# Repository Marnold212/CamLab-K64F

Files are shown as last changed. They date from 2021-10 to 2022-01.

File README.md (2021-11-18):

# CamLab-K64F
Code for performing data acquisition with the FRDM-K64F microcontroller. Currently tested using Windows 10 and VS Code. 

## Cloning Git Repo

Since mbed-os folder is linked as a submodule, in order to compile code locally, you must use the command "git clone --recursive https://github.com/Marnold212/CamLab-K64F" to also clone the mbed-os from its respective repo.  

## Flashing correct mbed Bootloader to K64F 

This may be need to be done for a new board, or a board that was previously used with a different program such as NXP MCUXpresso. Also may be required if there is a memory issue which crashes the board. Follow instructions on https://daplink.io/?board=FRDM-K64F.

- Copy of bootloader .bin file which is saved in the main branch of this repository 
- Reset button on K64F while connecting to PC via USB - should mount as bootloader 
- Drag and drop the .bin firmware file to the board and wait roughly 60 seconds
- unplug and should now have the correct firmware 

## Windows Toolchain 

Breif description of tools required for this project  

- **Git** https://git-scm.com/download/win
- **Python 3.9** was the version I used - Can use a Virtual Environment
  - Note that on powershell I needed to enable scripts (see below)
- **mbed-CLI 1** since mbed-CLI2 doesn't seem to have the same feature set 
- **GNU Arm Embedded Toolchain** version depends on which mbed-CLI version is used can be found on mbed-CLI documentation
  - Note that path must be specified in mbed config 
  - Name slightly for different versions - beware if changing path names 

## Installing GNU Arm Embedded Toolchain

On windows download .exe from https://developer.arm.com/tools-and-software/open-source-software/developer-tools/gnu-toolchain/gnu-rm/downloads for correct major version - Currenty latest supported is v9 2019-q4-major. Run the .exe file and select the add to PATH option in the installer. Check path of installation specifically the bin file as this path will be required. 

## Installing mbed-CLI 1

Use the package manager [pip](https://pip.pypa.io/en/stable/) to install mbed command line tools for compiling and flashing mbed device. Note that special instructions required to install mercurial with a venv(virtual environment) due to Visual C++ requirement - see below. 

```bash
pip install mbed-cli
pip install mbed-greentea
pip install mercurial
pip install mbed-ls
pip install mbed-tools
```

## Installing required packages for mbed-CLI 1
mbed-cli has a number of dependencies which are required for various tasks such as compiling. One way to install these is to import either an example program or just mbed-os as described below. Within root directory of mbed-os/ there is a requirements.txt file so 'pip install (-U) -r requirements.txt' should work otherwise can install manually. When trying to compile a project it should list any missing packages, although this method may lead to issues with versions and dependencies. 

## Basic mbed-CLI Usage 

mbed-CLI runs in command-line such as a vs-code terminal or windows CMD. Look at the documentation for [mbed-CLI 1](https://os.mbed.com/docs/mbed-os/v6.15/build-tools/mbed-cli-1.html) for further details. Note that to my knowledge pyOCD does not work on Raspberry Pi architechture so tools such as flashing board or debugging don't work.

Note that compiling a project for the 1st time will take a very long time due to the number of libraries in mbed-os which need to be compiled, however the 2nd time will be much quicker, as only modified classes need to be recompiled. 

```python
# lists available commands 
mbed 

# After cloning this project, may need to create a local mbed project within folder 
mbed new . 

# set the path for the GCC Toolchain - this path depends on your installation 
mbed config --global GCC_ARM_PATH "C:\Program Files (x86)\GNU Arm Embedded Toolchain\10 2020-q4-major\bin"

# returns list of connected devices 
mbed detect

# returns current compilation config 
mbed config --list

# set local toolchain to GCC_ARM (Use -G flag for global config)
mbed -t GCC_ARM

# set local device to either detect or k64f (Use -G flag for global config)
mbed -m detect
mbed -m k64f

# imports example project 
mbed import https://github.com/ARMmbed/mbed-os-example-blinky 

# imports mbed-os library
mbed import mbed-os 

# Compile an mbed project (-t and -m not required if aready set within project)
# -f flag automatically flashes .bin file if there is a suitable device connected 
# --sterm option opens a terminal in the command line with default settings (9600)
mbed compile -t <toolchain> -m <target> -f --sterm 
```

## Python Virtual Environments (venv)

To avoid clashes with dependencies, create a virtual environment. Activate the venv by running the activation script, exit by running "deactivate". 
There may be issues running the activation script using powershell due to permissions, if so use the command "Set-ExecutionPolicy Unrestricted -Scope Process". 

```bash
pyton -m venv venv 
pip list 
venv/Scripts/activate 
```

Had [issues](https://github.com/CodeForBuffalo/affordable_water/issues/11) installing mercurial using venv due to lack of Microsoft Visual C++ 14.0, even though I already had Microsoft Visual C++ 14 installed on PC. To solve, install build tools for Visual Studio from https://visualstudio.microsoft.com/downloads/, go to individual components and install: 
* Windows 10 SDK 
* C++ CMake Tools 
* MSVC (latest version) C++ x64/86 build tools 
* C++/CLI suppport 

## Debugging K64F 

The K64F has an on-chip debugger that allows debugging of program. The only configuration I have successfully implemented is pyOCD using VS Code as I couldn't get OpenOCD to work on this board. Install pyOCD using pip as shown below ensuring no issues with dependencies, and check it is working by running commands "pyocd list" or "pyocd-gdbserver" in CMD with the K64F connected. 

```bash
pip install pyOCD 
```
We now need to configure VS Code in order to allow us to run the debugger. 

## Configuring VS-Code 

Configuration for vs-code to allow for debugging of K64F as well as building of code without debugging which I use to save having to write command every time I compile code. Requires the following:
- VS Code Extensions
  - C/C++
  - cortex-debug (marcus25)
- Modification of the .vscode/ folder in the project directory 
  - launch.json
  - tasks.json 
  - c_cpp_properties.json

There a few different methods for adding a .vscode/ folder to a project. The easiest would be to modify the one in this reopository for particular computer, another option in vs code is to attempt "Run and Debug" without one it should create a template. Also you could use the mbed command "mbed export -i vscode_gcc_arm -m K64F --profile mbed-os/tools/profiles/debug.json".

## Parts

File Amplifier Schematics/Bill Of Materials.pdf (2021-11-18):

## Bill Of Materials for UKCRIC-NRFIS LabJack Extn Bd

Design Title | UKCRIC-NRFIS LabJack Extn Bd
Author | MW
Document Number | 2011101
Revision | B
Design Created | 15 April 2021

### Design Last Modified 15 April 2021 Total Parts In Design 129

31 Resistors
Quantity References | BOM Value Value | Tol | Package Description | Key
Properties
Manufacturer Manufacturer's PN | Supplier | Order
Code
2 | R1-R2 | 470R | 470R | 1% | 0805 | Thick Film SMTResistor 150V
Preferred | Panasonic | ERJ6ENF4701V | Farnell | 230-3515
3 | R3-R4,R7 | 0R | 0R | 5% | 0805 | Thick Film SMTResistor 150V
Panasonic | ERJ-6GEY0R00V | Farnell | 205-7661
2 | R5-R6 | 2k7 | 2k7 | 1% | 0805 | Thick Film SMTResistor 150V
Panasonic | ERJ6ENF2701V | Farnell | 230-3597
16 | R101-R102,R201-R202,R301- | 3k9 | 3k9 | 1% | 0805 | Thick Film | Preferred | Panasonic | ERJ6ENF3901V | Farnell | 230-3613
R302,R401-R402,R501-R502, | | | SMTResistor
R601-R602,R701-R702,R801- | | | 150V
R802
8 | R103,R203,R303,R403,R503,
R603,R703,R803
100R | 100R | 1% | 0805 | Thick Film
SMTResistor
150V
Preferred | Panasonic | ERJ6ENF1000V | Farnell | 230-3442

Sub-totals:
62 Capacitors
Quantity References | BOM Value Value | Tol | Package Description | Key
Properties
Manufacturer Manufacturer's PN | Supplier | Order
Code
2 | C1-C2 | 4u7 | 4.7u | 20% 1206 | 25V Multilayer
X7R
Kemet | C1206C475M3RACTU Farnell | 282-0941
2 | C3-C4 | 1u0 | 1u0 | 10% | 1206 | 100V Multilayer X7R
AVX | 12061C105KAT2A | Farnell | 165-7939
2 | C5-C6 | 100n | 100n | 10% 0805 | Ceramic 50V
| | | | | | X7R
Preferred | Kemet | C0805C104K5RAC | Farnell | 141-4664

16 | C101-C102,C201-C202,C301- | 1n0 | 1n0 | 5% | 0805 | 50V Ceramic | Kemet | C0805C102J5GACTU | Farnell | 141-4658
C302,C401-C402,C501-C502, | | | COG
C601-C602,C701-C702,C801-
C802
16 | C103,C105,C203,C205,C303,
C305,C403,C405,C503,C505,
C603,C605,C703,C705,C803,
C805
10n | 10n | 10% 0805 | Ceramic 50V
X7R
Kemet | C0805C103K5RAC | Farnell | 141-4662
16 | C104,C106,C204,C206,C304, | 330n | 330n | 10% | 0805 | Ceramic 50V | Kemet | C0805C334K5RACTU | Farnell | 233-2405
C306,C404,C406,C504,C506, | | | X7R
C604,C606,C704,C706,C804,
C806
8 | C107,C207,C307,C407,C507,
C607,C707,C807
47n | 10% | Kemet | C0805C473K5RAC | Farnell | 141-4697

Sub-totals:
12 Integrated Circuits
Quantity References | BOM Value Value | Tol | Package Description | Key
Properties
Manufacturer Manufacturer's PN | Supplier | Order
| | | | | Code
1 | U1 | 5V-
>+5V,-5V
NTA0505MC | 10-pin
SMT

DC/DC
Converter
| | Murata | NTA0505MC | Farnell | 102-1591
1 | U2 | 5V-
>+12V,-12V
NTA0512MC | 10-pin
SMT

DC/DC
Converter
| | Murata | NTA0512MC | Farnell | 102-1593
2 | U3-U4 | Quad | SN74HCT125M | 14-pin
SOIC

Tristate buffer VIH >
2.0V
| | Texas Instruments | SN74HCT125M | Farnell | 312-1014
8 | U101,U201,U301,U401,U501,
U601,U701,U801
Precision | AD623ARZ | 8-pin
SOIC

Instrumentation
Amp
| | Analog Devices | AD623ARZ | RS Components | 806-5522

Sub-totals:
4 Wound Components
Quantity References | BOM Value Value | Tol | Package Description | Key
Properties
Manufacturer Manufacturer's PN | Supplier | Order
| | | | | Code
2 | L1-L2 | 10uH | SMT | 500mA Power
Inductor
| | Murata | 82103C | Farnell | 284-0105
2 | L3-L4 | 47uH | SMT | 250mA Power
Inductor
| | Murata | 82473C | Farnell | 211-2805

Sub-totals:
12 Connectors
Quantity References | BOM Value Value | Tol | Package Description | Key
Properties
Manufacturer Manufacturer's PN | Supplier | Order
| | | | | Code
1 | J1 | 40-way | M20-9982045 | 0.1"
pitch
dual row}
Pin header | Harwin | M20-9982045 | Farnell | 322-6016

1 | J2 | 16-way | M20-9980845 | 0.1"
pitch
dual row
Pin header | Harwin | M20-9980845 | Farnell | 102-2239
2 | J3-J4 | 15-pin | 171-015-113R911 | 15-pin Vertical
D-SUB Male | Norcomp | 171-015-113R911 | RS
Components

174-8712

8 | J101,J201,J301,J401,J501, J601,J701,J801 | 15-pin | 171-015-213R911 | 15-pin Vertical
D-SUB Female | Norcomp | 171-015-213R911 | RS
Components

174-8730

Sub-totals:
8 Miscellaneous
Quantity References | BOM Value Value | Tol | Package Description | Key
Properties
Manufacturer Manufacturer's PN | Supplier | Order
Code
2 | FU1-FU2 | 250mA | 0ZCJ0025FF2E | 1206 | SMT Fuse | Bel Power Solutions
0ZCJ0025FF2E | Farnell | 283-4885
3 | Z1,Z3,Z5 | | 0V | PCB feature
Test point | None | None | None | None
1 | Z2 | | PGND | PCB feature
Test point | None | None | None | None
1 | Z4 | | GND | PCB feature
Test point | None | None | None | None
1 | Z6 | | EARTH | PCB feature
Test point | None | None | None | None

Sub-totals:

Totals:

15 April 2021 13:20:37

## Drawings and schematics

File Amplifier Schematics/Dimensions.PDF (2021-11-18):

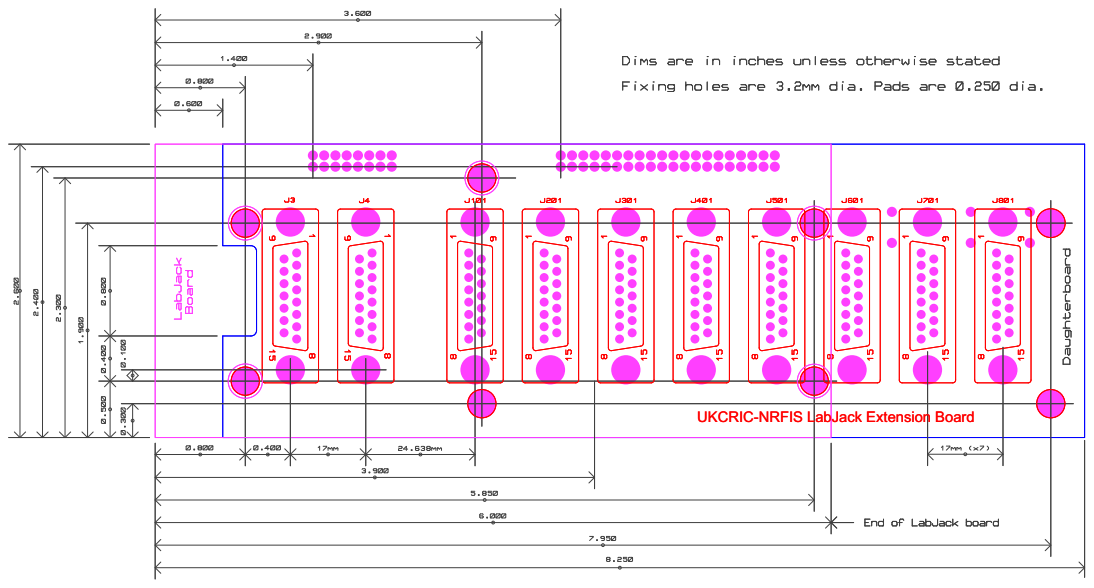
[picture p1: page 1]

UKCRIC-NRFIS LabJack Extension Board

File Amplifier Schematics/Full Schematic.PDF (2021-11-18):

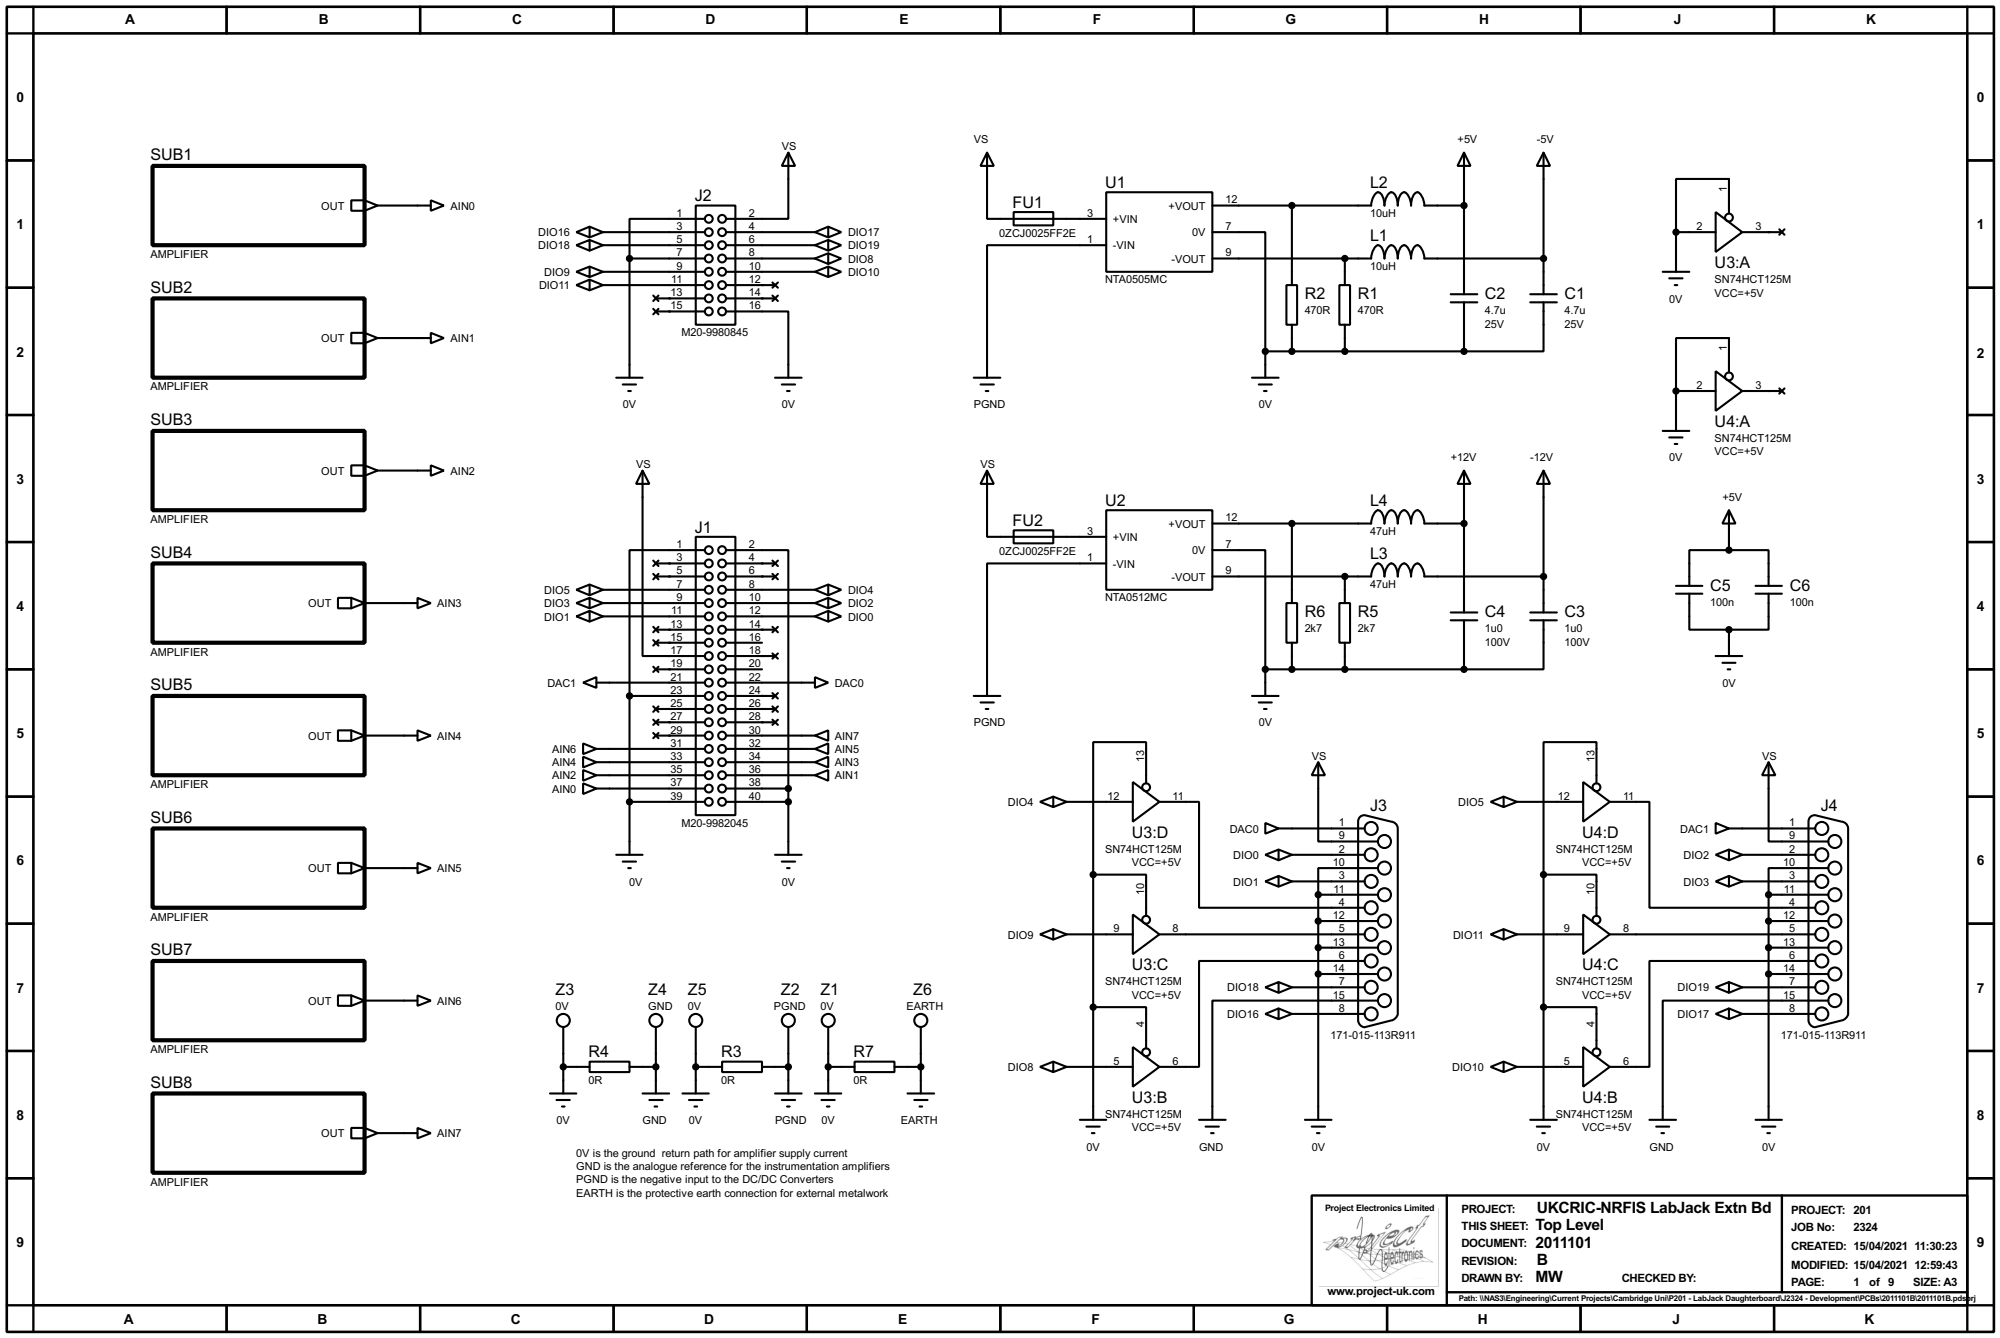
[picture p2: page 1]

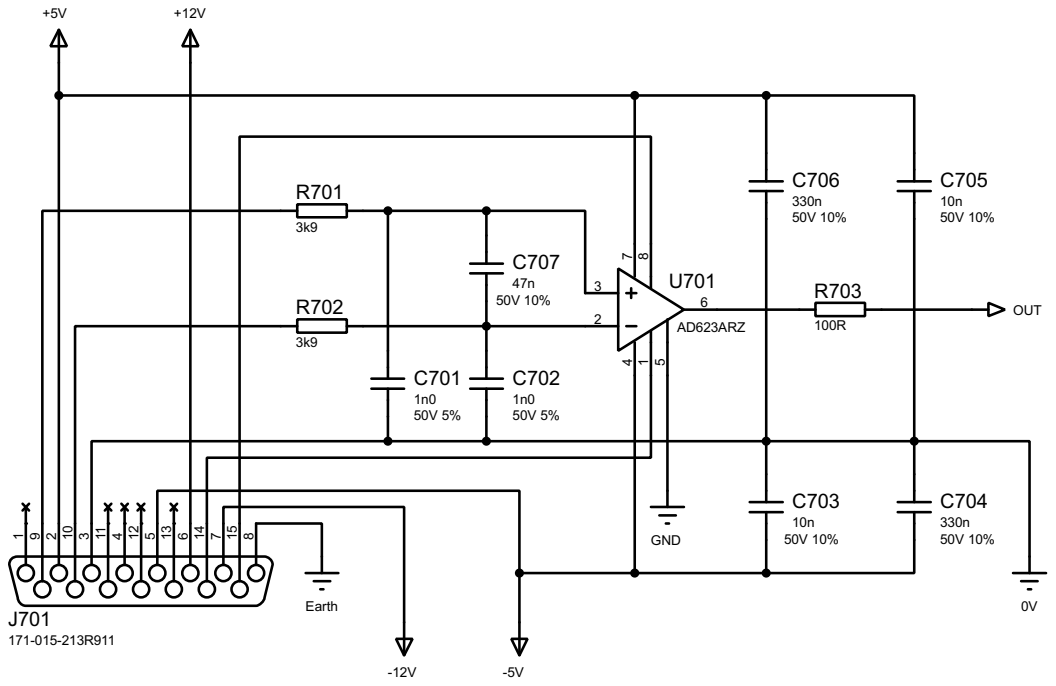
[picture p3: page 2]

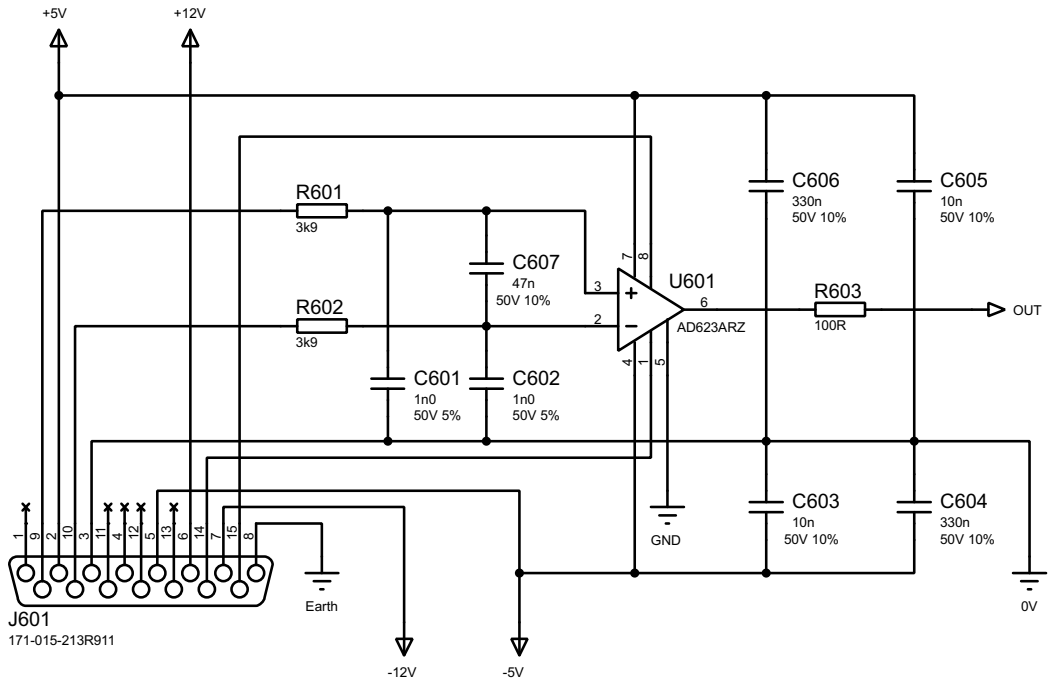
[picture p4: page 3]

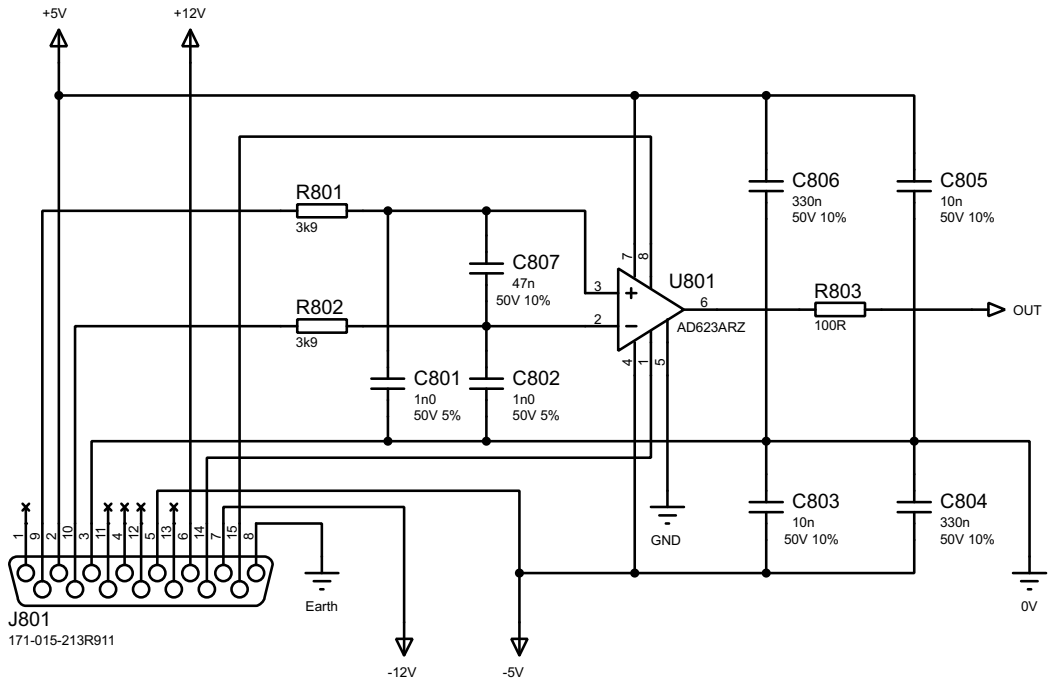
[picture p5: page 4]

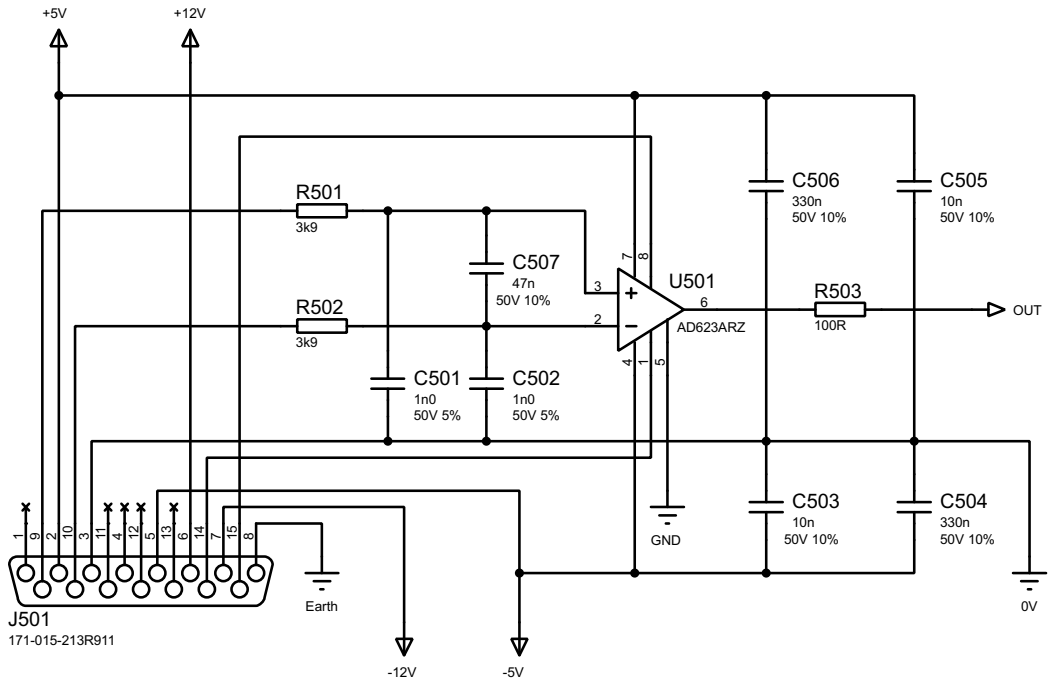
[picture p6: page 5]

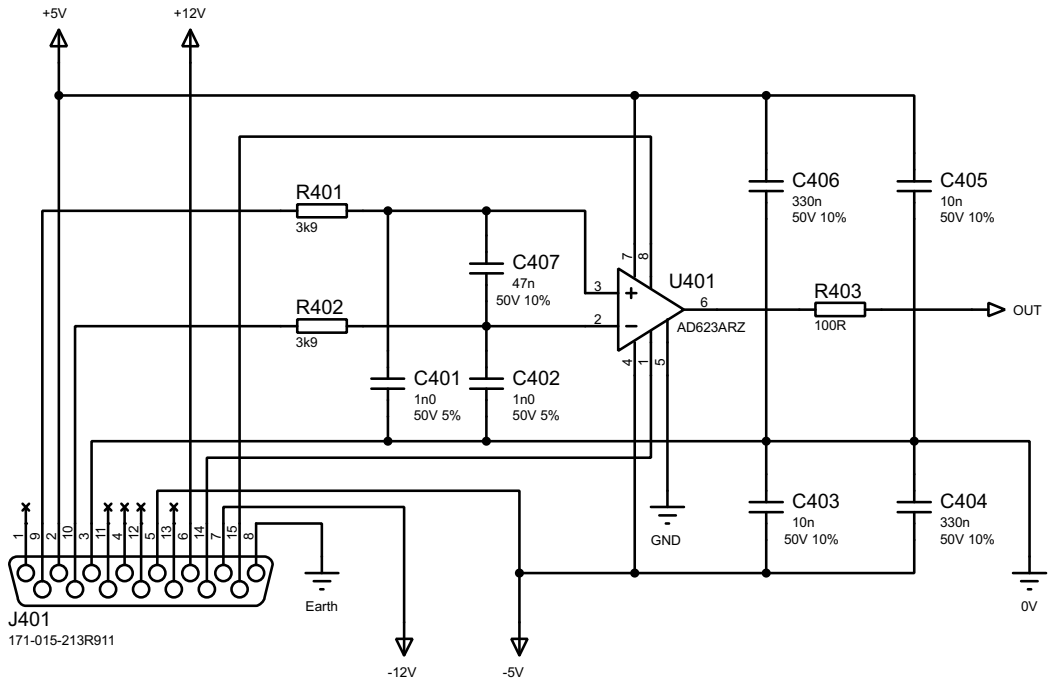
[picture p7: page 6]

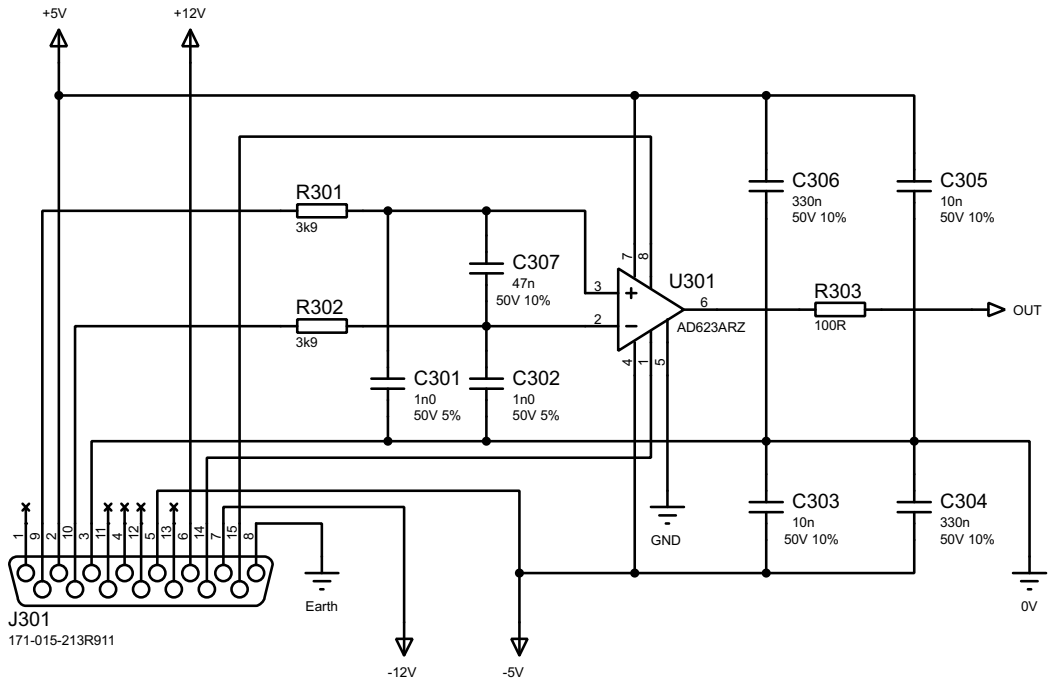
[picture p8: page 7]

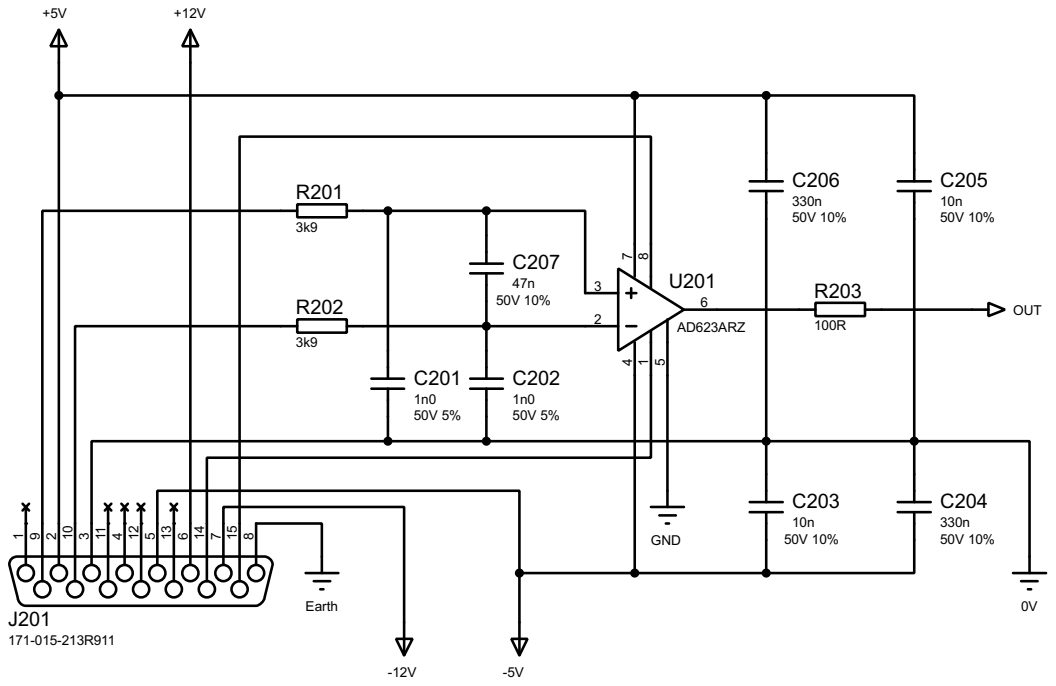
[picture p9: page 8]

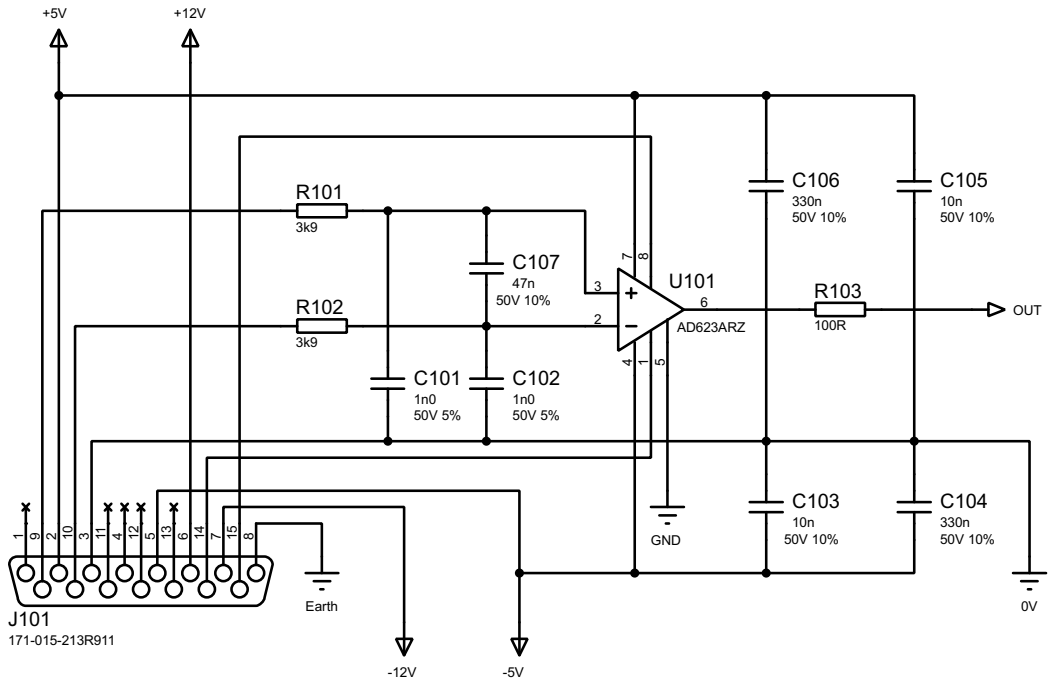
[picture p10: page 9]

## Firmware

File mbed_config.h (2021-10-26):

/*
 * mbed SDK
 * Copyright (c) 2017 ARM Limited
 *
 * Licensed under the Apache License, Version 2.0 (the "License");
 * you may not use this file except in compliance with the License.
 * You may obtain a copy of the License at
 *
 * http://www.apache.org/licenses/LICENSE-2.0
 *
 * Unless required by applicable law or agreed to in writing, software
 * distributed under the License is distributed on an "AS IS" BASIS,
 * WITHOUT WARRANTIES OR CONDITIONS OF ANY KIND, either express or implied.
 * See the License for the specific language governing permissions and
 * limitations under the License.
 */

// Automatically generated configuration file.
// DO NOT EDIT, content will be overwritten.

#ifndef __MBED_CONFIG_DATA__
#define __MBED_CONFIG_DATA__

// Configuration parameters
#define MBED_CONF_ALT1250_PPP_BAUDRATE                                        115200                                                                                           // set by library:ALT1250_PPP
#define MBED_CONF_ALT1250_PPP_PROVIDE_DEFAULT                                 0                                                                                                // set by library:ALT1250_PPP
#define MBED_CONF_ATMEL_RF_ASSUME_SPACED_SPI                                  0                                                                                                // set by library:atmel-rf
#define MBED_CONF_ATMEL_RF_FULL_SPI_SPEED                                     7500000                                                                                          // set by library:atmel-rf
#define MBED_CONF_ATMEL_RF_FULL_SPI_SPEED_BYTE_SPACING                        250                                                                                              // set by library:atmel-rf
#define MBED_CONF_ATMEL_RF_IRQ_THREAD_STACK_SIZE                              1024                                                                                             // set by library:atmel-rf
#define MBED_CONF_ATMEL_RF_LOW_SPI_SPEED                                      3750000                                                                                          // set by library:atmel-rf
#define MBED_CONF_ATMEL_RF_PROVIDE_DEFAULT                                    0                                                                                                // set by library:atmel-rf
#define MBED_CONF_ATMEL_RF_USE_SPI_SPACING_API                                0                                                                                                // set by library:atmel-rf
#define MBED_CONF_CELLULAR_AT_HANDLER_BUFFER_SIZE                             32                                                                                               // set by library:cellular
#define MBED_CONF_CELLULAR_CONTROL_PLANE_OPT                                  0                                                                                                // set by library:cellular
#define MBED_CONF_CELLULAR_DEBUG_AT                                           0                                                                                                // set by library:cellular
#define MBED_CONF_CELLULAR_MAX_CP_DATA_RECV_LEN                               1358                                                                                             // set by library:cellular
#define MBED_CONF_CELLULAR_PRESENT                                            1                                                                                                // set by library:cellular
#define MBED_CONF_CELLULAR_RANDOM_MAX_START_DELAY                             0                                                                                                // set by library:cellular
#define MBED_CONF_CELLULAR_USE_APN_LOOKUP                                     0                                                                                                // set by library:cellular
#define MBED_CONF_CELLULAR_USE_SMS                                            0                                                                                                // set by library:cellular
#define MBED_CONF_DRIVERS_OSPI_CSN                                            OSPI_FLASH1_CSN                                                                                  // set by library:drivers
#define MBED_CONF_DRIVERS_OSPI_DQS                                            OSPI_FLASH1_DQS                                                                                  // set by library:drivers
#define MBED_CONF_DRIVERS_OSPI_IO0                                            OSPI_FLASH1_IO0                                                                                  // set by library:drivers
#define MBED_CONF_DRIVERS_OSPI_IO1                                            OSPI_FLASH1_IO1                                                                                  // set by library:drivers
#define MBED_CONF_DRIVERS_OSPI_IO2                                            OSPI_FLASH1_IO2                                                                                  // set by library:drivers
#define MBED_CONF_DRIVERS_OSPI_IO3                                            OSPI_FLASH1_IO3                                                                                  // set by library:drivers
#define MBED_CONF_DRIVERS_OSPI_IO4                                            OSPI_FLASH1_IO4                                                                                  // set by library:drivers
#define MBED_CONF_DRIVERS_OSPI_IO5                                            OSPI_FLASH1_IO5                                                                                  // set by library:drivers
#define MBED_CONF_DRIVERS_OSPI_IO6                                            OSPI_FLASH1_IO6                                                                                  // set by library:drivers
#define MBED_CONF_DRIVERS_OSPI_IO7                                            OSPI_FLASH1_IO7                                                                                  // set by library:drivers
#define MBED_CONF_DRIVERS_OSPI_SCK                                            OSPI_FLASH1_SCK                                                                                  // set by library:drivers
#define MBED_CONF_DRIVERS_QSPI_CSN                                            QSPI_FLASH1_CSN                                                                                  // set by library:drivers
#define MBED_CONF_DRIVERS_QSPI_IO0                                            QSPI_FLASH1_IO0                                                                                  // set by library:drivers
#define MBED_CONF_DRIVERS_QSPI_IO1                                            QSPI_FLASH1_IO1                                                                                  // set by library:drivers
#define MBED_CONF_DRIVERS_QSPI_IO2                                            QSPI_FLASH1_IO2                                                                                  // set by library:drivers
#define MBED_CONF_DRIVERS_QSPI_IO3                                            QSPI_FLASH1_IO3                                                                                  // set by library:drivers
#define MBED_CONF_DRIVERS_QSPI_SCK                                            QSPI_FLASH1_SCK                                                                                  // set by library:drivers
#define MBED_CONF_DRIVERS_UART_SERIAL_RXBUF_SIZE                              256                                                                                              // set by library:drivers
#define MBED_CONF_DRIVERS_UART_SERIAL_TXBUF_SIZE                              256                                                                                              // set by library:drivers
#define MBED_CONF_ESP8266_BUILT_IN_DNS                                        0                                                                                                // set by library:esp8266
#define MBED_CONF_ESP8266_DEBUG                                               0                                                                                                // set by library:esp8266
#define MBED_CONF_ESP8266_POWER_OFF_TIME_MS                                   3                                                                                                // set by library:esp8266
#define MBED_CONF_ESP8266_POWER_ON_POLARITY                                   0                                                                                                // set by library:esp8266
#define MBED_CONF_ESP8266_POWER_ON_TIME_MS                                    3                                                                                                // set by library:esp8266
#define MBED_CONF_ESP8266_PROVIDE_DEFAULT                                     0                                                                                                // set by library:esp8266
#define MBED_CONF_ESP8266_SERIAL_BAUDRATE                                     115200                                                                                           // set by library:esp8266
#define MBED_CONF_ESP8266_SNTP_ENABLE                                         0                                                                                                // set by library:esp8266
#define MBED_CONF_ESP8266_SNTP_SERVER0                                        ""                                                                                               // set by library:esp8266
#define MBED_CONF_ESP8266_SNTP_SERVER1                                        ""                                                                                               // set by library:esp8266
#define MBED_CONF_ESP8266_SNTP_SERVER2                                        ""                                                                                               // set by library:esp8266
#define MBED_CONF_ESP8266_SNTP_TIMEZONE                                       0                                                                                                // set by library:esp8266
#define MBED_CONF_ESP8266_SOCKET_BUFSIZE                                      8192                                                                                             // set by library:esp8266
#define MBED_CONF_EVENTS_PRESENT                                              1                                                                                                // set by library:events
#define MBED_CONF_EVENTS_SHARED_DISPATCH_FROM_APPLICATION                     0                                                                                                // set by library:events
#define MBED_CONF_EVENTS_SHARED_EVENTSIZE                                     768                                                                                              // set by library:events
#define MBED_CONF_EVENTS_SHARED_HIGHPRIO_EVENTSIZE                            256                                                                                              // set by library:events
#define MBED_CONF_EVENTS_SHARED_HIGHPRIO_STACKSIZE                            1024                                                                                             // set by library:events
#define MBED_CONF_EVENTS_SHARED_STACKSIZE                                     2048                                                                                             // set by library:events
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

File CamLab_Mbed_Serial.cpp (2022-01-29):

#include "CamLab_Mbed_Serial.h"
#include "mbed.h"

void CamLab_Mbed_Serial::Init_Serial(void){
    // Create a BufferedSerial object with a default baud rate.
    // BufferedSerial serial_port(USBTX, USBRX); // May be able to have full-duplex if no arguments given to buffered Serial class 
    // Set desired properties (115200-8-N-1).    
    serial_handle->set_baud(Serial_baudrate);
    serial_handle->set_format(
        /* bits */ 8,
        /* parity */ BufferedSerial::None,
        /* stop bit */ 1
    );
}

void CamLab_Mbed_Serial::Init_SPI(void){
    // For now use mbed code to initialise all clocks/registers 
    DigitalOut Device_1_CS(D15);
    Device_1_CS = 1;
}

void CamLab_Mbed_Serial::Receive_Serial_Data(void){ // Look for more efficient implemmentation 
    // ThisThread::sleep_for(4ms); // Needed to get full input - 10ms just arbitrary value - but errors if only 1ms
    wait_us(3500);  // Wait time in us for 8*32 bits to arrive at a rate of 115200 
    // wait_us(us_wait_32_bytes_Serial); 
}

int CamLab_Mbed_Serial::Read_Serial_Buffer(void){ 
// Reads Serial buffer to buf[], while returning the number of bytes received 
    return serial_handle->read(buf_serial, sizeof(buf_serial));
}

void CamLab_Mbed_Serial::Write_Serial_Message(char *reg, int num){
    serial_handle->write(reg, num);
}

void CamLab_Mbed_Serial::Append_EOL_Char(int Num_Reply_Bytes)
{
    buf_serial[Num_Reply_Bytes - 1] = '\n';
}

void CamLab_Mbed_Serial::Serial_Response(void){
    int num_in = 0;
    // ThisThread::sleep_for(1s);
    if (serial_handle->readable()) {
        Receive_Serial_Data(); // Wait for a given time to receive all data ?? Look for more efficient implemmentation  
        if ((num_in = serial_handle->read(buf_serial, sizeof(buf_serial)))) { // Check there is something other than "\n" in the buffer AKA num_1 != 0
            // if(buf_serial[0] == 0x30){
            //     if(num_in == 6){ // 1 Command byte (030), 4 address bytes (8 Hex Digits), 1 End of Line ("\n")
            //         Serial_Read_Register();
            //     }
            // }  
            if(buf_serial[0] == Read_32_Reg_Instr && num_in == Read_32_Expected_Bytes){ //  
                Read_32_Reg_Response();
            }
            else if(buf_serial[0] == Read_16_Reg_Instr && num_in == Read_16_Expected_Bytes){
                Read_16_Reg_Response();
            }
            else if(buf_serial[0] == Read_8_Reg_Instr && num_in == Read_8_Expected_Bytes){
                Read_8_Reg_Response();
            }
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

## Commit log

2021-11-18 Amplifier Board Schematics
    [2011101B - CADCAM Bottom Assembly.GBR, 2011101B - CADCAM Bottom Copper.GBR, 2011101B - CADCAM Bottom SMT Paste.GBR, 2011101B - CADCAM Bottom Silk Screen.GBR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]
2021-12-05 Added Further Device Support
2022-01-20 Sample Time
2022-01-27 Config file - allow printf() to work with float
